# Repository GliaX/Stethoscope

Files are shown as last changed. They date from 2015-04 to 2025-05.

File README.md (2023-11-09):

Stethoscope
===========

This project aims to create a research-validated stethoscope whose plans are 
available freely and openly. The goal is for the bell to cost ~USD$1-2 to produce, 
and the rest of the stethoscope to cost approximately the same. You can see the peer-reviewed publication relating to this stethoscope's validation here:

http://journals.plos.org/plosone/article?id=10.1371/journal.pone.0193087

Currently, the stethoscope resulting from this project functions as well as the 
market gold standard, the Littmann Cardiology III.

Bill of Materials
=================

**Printed parts:**
* 1 stethoscope head (head.stl)
* 2 ear tubes (eartube.stl)
* 1 Y-piece (y_piece.stl)
* 1 Spring (spring.stl)
* 1 Ring (ring.stl)

**Other hardware:**
Some vendors are suggested.
* 40cm - 50cm Silicone 13mm (preferred) or 12mm OD, 8mm ID, 50 durometer
  * [8MM I.D X 13MM O.D NGP60 Clear Translucent Silicone Hose Pipe Tubing](https://www.advancedfluidsolutions.co.uk/8mm-id-x-13mm-od-clear-transulcent-silicone-hose-pipe-tubing-2482-p.asp) (USD$7.34/meter)

* 20cm Silicone 8mm (preferred) or 6mm OD, 4mm ID (cut into 10cm pieces), 60 durometer
  * [4mm ID x 8mm OD](https://www.advancedfluidsolutions.co.uk/4mm-id-x-8mm-od-clear-transulcent-silicone-hose-pipe-tubing-2454-p.asp)

* Diaphragm: 40mm diameter cut from a report cover with approx 0.35mm plastic sheet
  * [In Business Report Covers](https://www.amazon.com/dp/B0CJCBC86X?_encoding=UTF8&psc=1&ref_=cm_sw_r_ud_dp_CY0Q8HRSQEBTA39H9VF2)(USD$8.99)
  * You can cut the diaphragm by hand or with a stamp like [this one](https://www.amazon.ca/Karujimu-ki-jumbo-craft-circle-CN45004/dp/B001CBY41W)

* Earbuds / Eartips: Any large-sized standard earbuds will do.
  * [Silicone Earbuds 7 Pairs - Large size](https://www.amazon.ca/gp/product/B006VELFJY)
 
**Optional hardware**:
* Metal spring for holding ear tubes together

Print Instructions
==================
**INFILL MUST BE 100%** **INFILL MUST BE 100%** **INFILL MUST BE 100%** **INFILL MUST BE 100%**

* Use PETG or ABS
* Layer height: 0.2mm
* Use PrusaSlicer 2.0 or above to import 3MF file
* Modify filament and printer settings as needed.
* **DO NOT MODIFY PRINT SETTINGS**
* Export and print

Troubleshooting
===============

* If the spring and eartubes do not fit well, go ahead and scale the spring as needed
* If the head and ring do not fit well, use caution as you may be modifying the acoustics. You can scale the head a little.

Notes
=====

* We do not use PLA due to deformation in heat and poor plastic quality in the spring causing early failure. PLA may be used, but the lifetime of the stethoscope will decrease significantly.

* We do not use brims, but you may print the eartubes and Y-pieces with a brim of 2mm to ensure that none of the parts lift off.

**INFILL MUST BE 100%** **INFILL MUST BE 100%** **INFILL MUST BE 100%.** Otherwise, the stethoscope will not produce a correct sound.

Assembly Instructions
=====================

See [this instructional video](https://www.youtube.com/watch?v=u-KNTc0POLA) for assembly instructions.

* Attach the diaphragm (40mm) to the stethoscope head.
* Attach the stethoscope head to the silicone tube.
* Attach the silicone tube to the Y-Piece.
* Attach spring to ear tubes.
* Attach the Y-piece to the ear tubes.
* Attach the ear tubes to the eartips / earbuds.
* Test the stethoscope as per the validation instructions.

Printing the inserts
====================
The inserts are included in the `manual` directory. Using 8.5 x 11 (Legal) paper,
they can be printed at 8.25" page width with 95% scale for the top print and 
90% scale for the bottom print using GIMP.

The top insert is cut at 14.5cm and again at 1cm creating two labels of 13.5cm height.
These inserts are printed on adhesive material.

The bottom insert is cut at a width of 20cm with a height cuts at 25cm, 15cm, 
13.5cm and 3.5cm creating 10cm x 20cm inserts.

Changing and creating SCAD files
================================

[CrystalSCAD](https://github.com/Joaz/CrystalScad) and [OpenSCAD](http://www.openscad.org/) 
were used to create all STL files. To recreate the stethoscope head, simply do:

``` shell
gem install crystalscad
ruby source_files/stethoscope_head/stethoscope_head.rb
```

The SCAD files output from CrystalSCAD are found in `source_files/stethoscope_head/output` and are named as follows:
* PrintableStethoscopeHead1Assembly_output.scad - The head

Mass Manufacturing
==================
We generally print 4 stethoscopes per plate to ensure that each stethoscope is created out of the same material.

Our serial numbering system consists of two parts. The last number part is the total number of unique stethoscopes created since day 1. All numbers before that dash are spool identifiers involved in that stethoscope. For example:

001-010 would be the tenth stethoscope made with the first spool in our inventory. If the first spool makes a total of 15 stethoscopes, then the first stethoscope of the second spool would be 002-016. If the twentieth stethoscope uses plastic from spool 002 and spool 003, it would be 002-003-020.

Other stethoscopes
==================
Others have made 3D printed stethoscopes too. See:
* https://www.youmagine.com/designs/stethoscope-chestpiece

Licensing notes
===============
As per our understanding, hardware is not covered by copyright. However, we present
our work under the TAPR OHL license insofar as it applies.

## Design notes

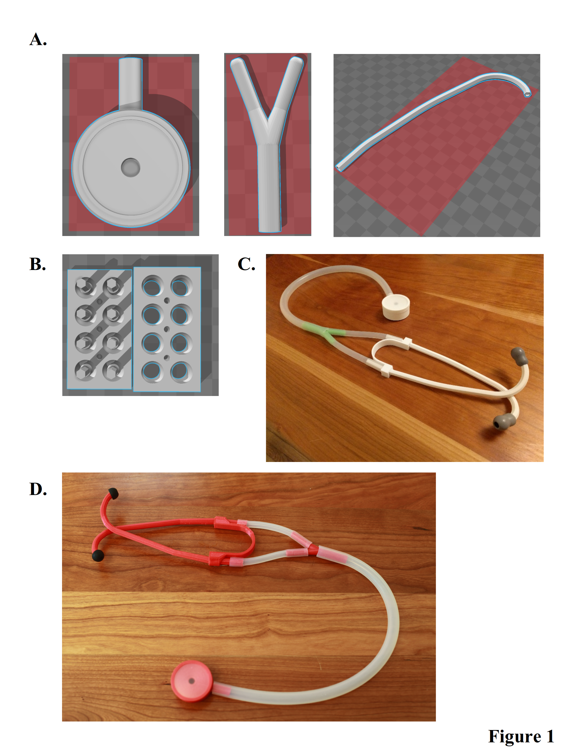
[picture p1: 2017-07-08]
Publication/Figure 1.tif

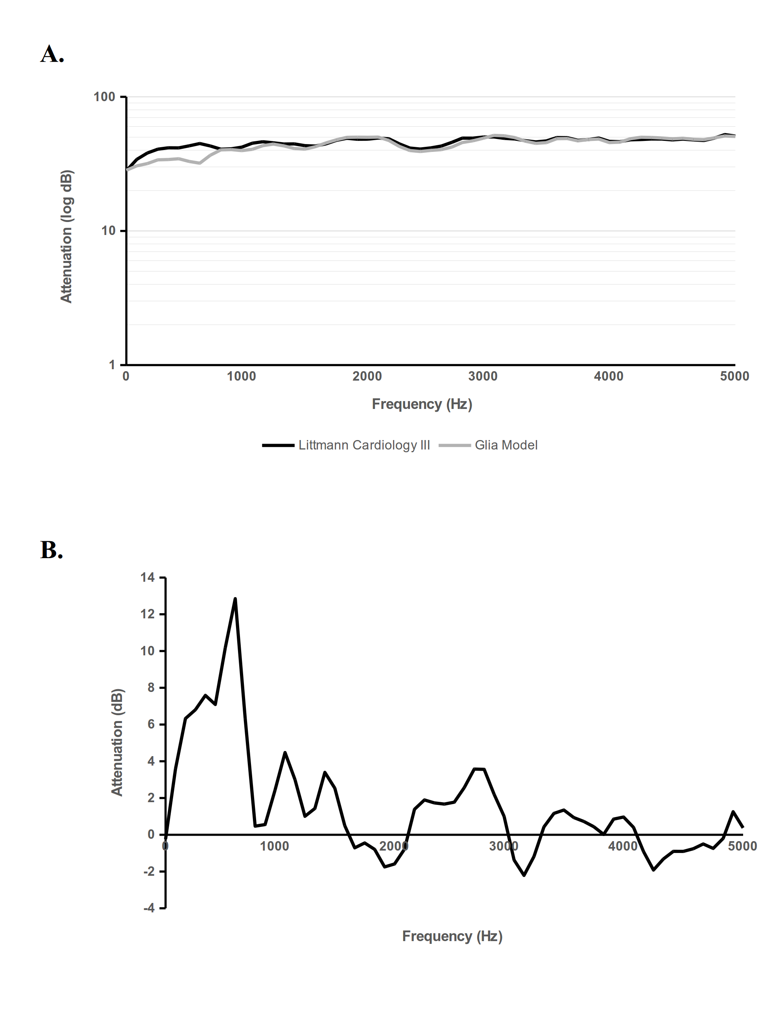
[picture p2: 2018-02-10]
publication/Fig2.tif

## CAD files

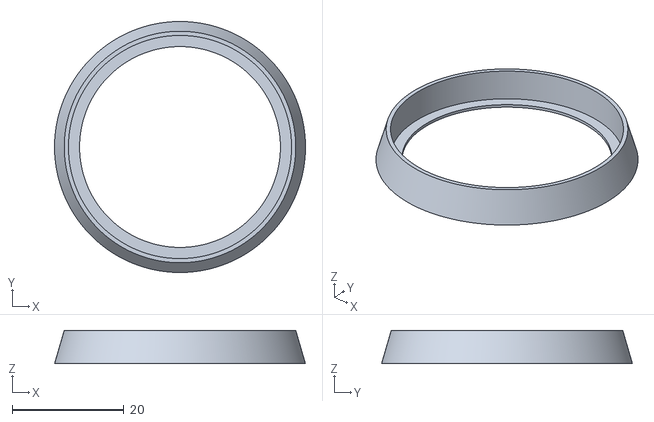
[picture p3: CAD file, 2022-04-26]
source_files/stl/ring.stl
45.0 x 45.0 x 6.00

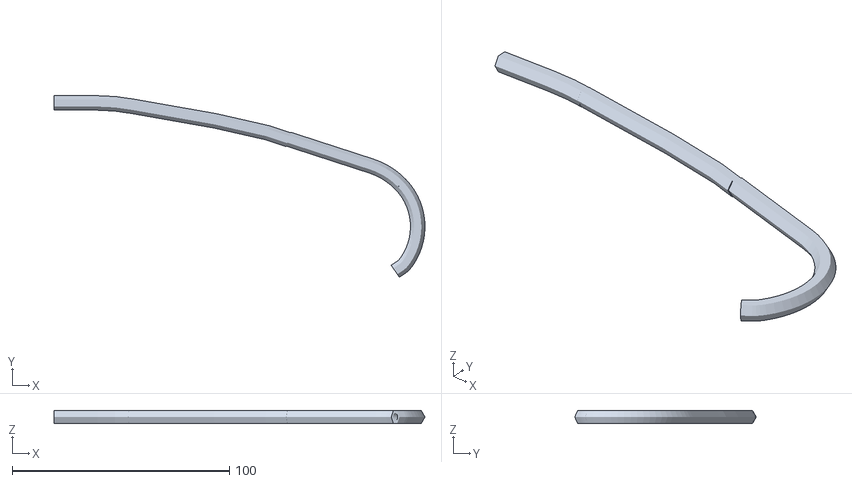
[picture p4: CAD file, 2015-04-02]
stethoscope_head/eartube.stl
170.8 x 83.6 x 5.80

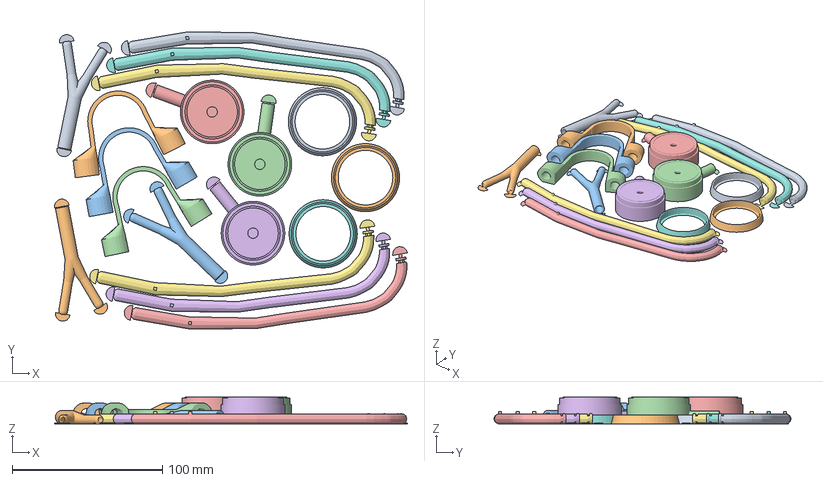
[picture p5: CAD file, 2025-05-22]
stethoscope_x3.3mf
235.1 x 198.1 x 17.9 mm
y_piece.stl
head.stl
eartube.stl x 2
Spring.stl
stetho-ring V2 FreeCad.stl

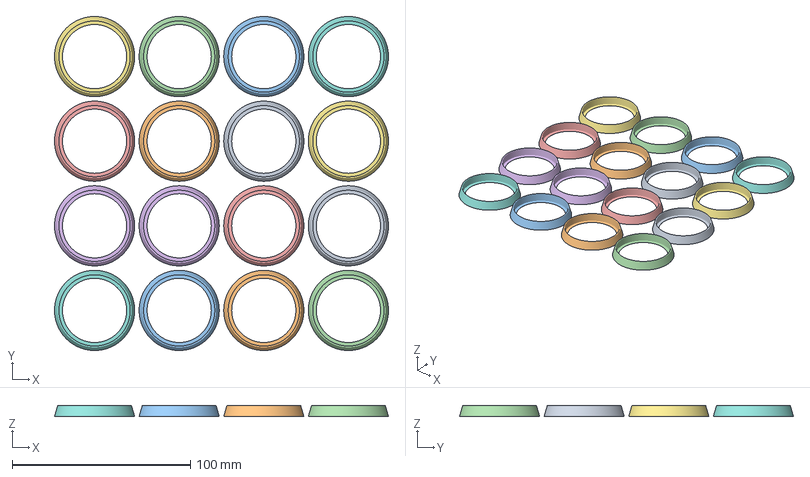
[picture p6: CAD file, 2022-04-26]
ring_x16.3mf
187.5 x 187.5 x 6.00 mm

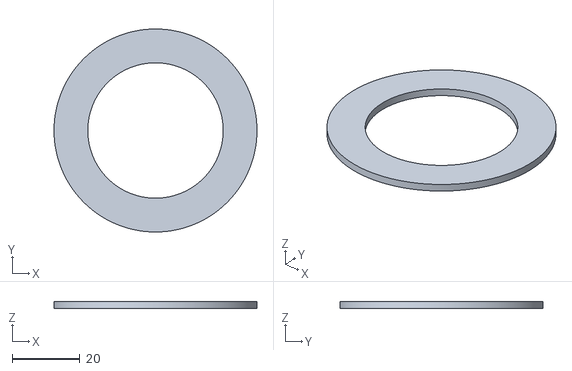
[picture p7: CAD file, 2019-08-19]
source_files/stl/Head Diaphragm Template(Cutting Guide).stl
60.0 x 60.0 x 2.00

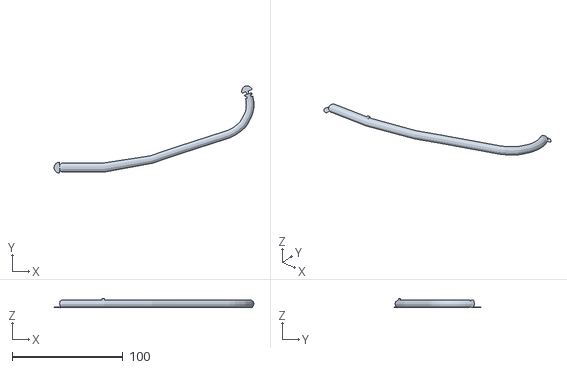
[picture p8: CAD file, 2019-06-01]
source_files/stl/eartube.stl
180.8 x 79.0 x 8.39

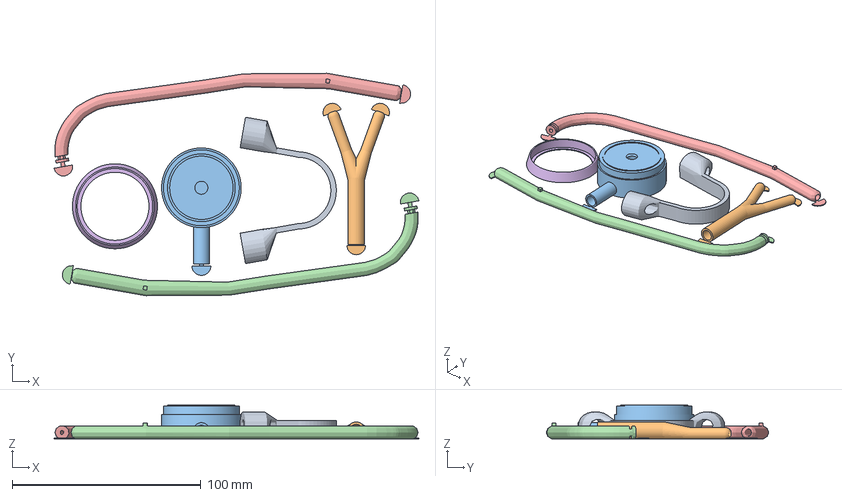
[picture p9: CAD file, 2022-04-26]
stethoscope_x1.3mf
193.3 x 117.8 x 17.9 mm
spring.stl
y_piece.stl
head.stl
eartube.stl
ring.stl

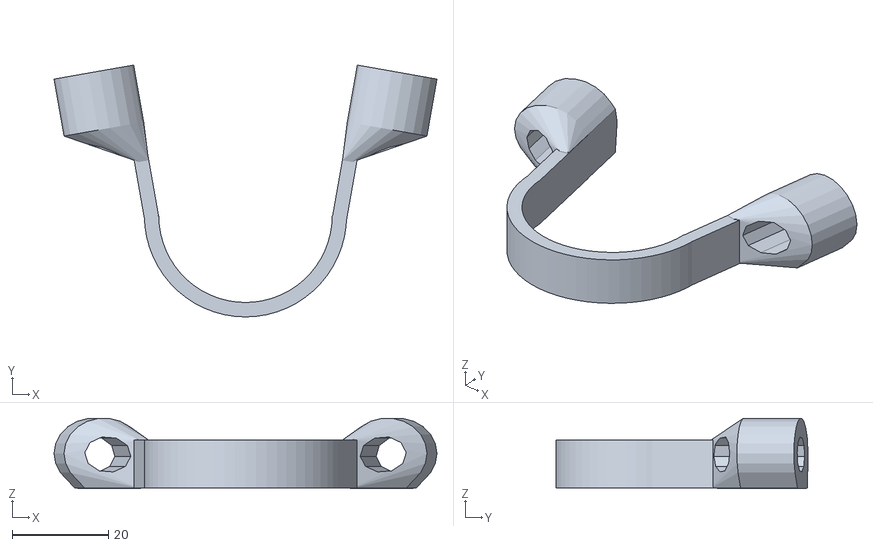
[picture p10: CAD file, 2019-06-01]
source_files/stl/spring.stl
79.5 x 52.3 x 14.6

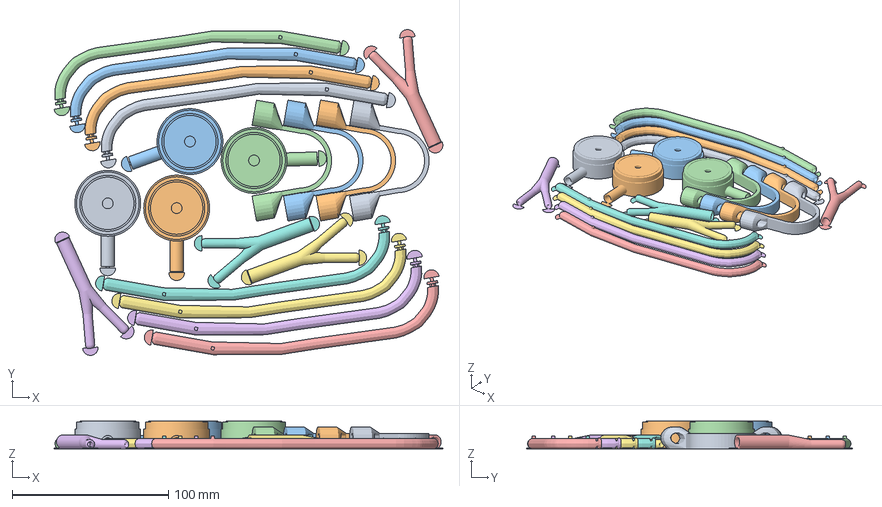
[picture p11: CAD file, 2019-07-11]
stethoscope_x4.3mf
249.1 x 208.8 x 17.9 mm
spring.stl
y_piece.stl
head.stl
eartube.stl

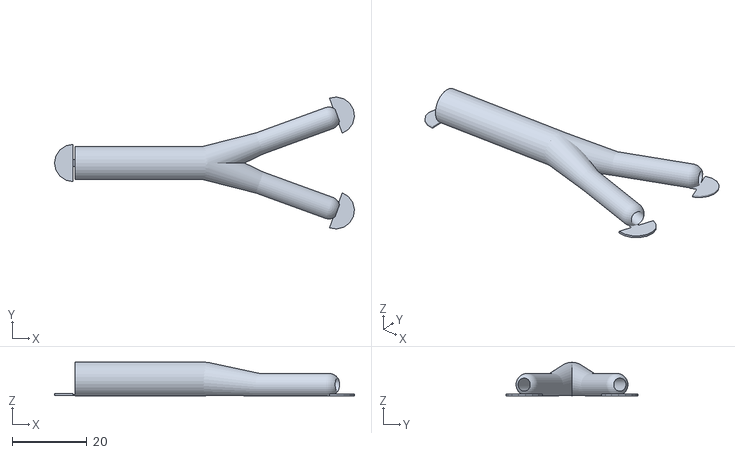
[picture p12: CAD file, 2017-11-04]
source_files/stl/y_piece.stl
80.3 x 35.3 x 9.00

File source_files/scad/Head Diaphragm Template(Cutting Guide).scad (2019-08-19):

//Head Diaphragm Template(Cutting Guide)
$outside_width = 30; //Radius of outside wall (mm)
$inside_width_wall = 20; //Inside radius of wall (mm)
$fn=360;


// Side wall

    difference() {
        cylinder(h = 2, r = $outside_width);
        cylinder(h = 2, r = $inside_width_wall);
    }

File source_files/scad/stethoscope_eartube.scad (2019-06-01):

/*
  The eartube is made of combination of spheres of 7mm diameter combined together to form its shape.
  The positioning of the spheres is taken by making array of x axis positions and array of y axis positions.
  The earbud area is different from the rest of the eartube body so it was made in different way. It is shaped and rotated to be in the right direction to snap fit standard earbuds.
  The inner hole in the eartube which should deliver the "sound" is made also from spheres but with 4mm  diameter with the same positioning of the outer shell spheres.
  The start and the end of the eartube have  mouse ears to prevent the eartube from warping during the printing process which can be removed easily by a sharp blade.
*/

/////////////////////////////////////////////////////////////
// Arrays for the X and Y positions of the spheres that make up the eartube

xarray=[-6,0,36.5,42.19,79.92,99.81,148.63,150,153.73,154.75,155.89,157.91,159.74,161.04,162.34,163.4,163.94,164.37,165.09,165.65,166.29,167.14,167.73,168.32,168.81,169.17,169.35,169.3,168.9,168.47,167.83,167.32];

yarray=[0,0,0,0.85,7.29,14.11,29.85,30.29,32.11,32.6,33.41,34.83,36.42,37.46,38.68,40.03,41.05,41.71,43.01,44.01,45.19,46.74,48.18,49.63,51.78,53.91,56.05,59.24,61.43,63.81,66.11,67.92];

// How much the earbud is rotated downward
earbud_rotation = -70;

// Width of piece connecting eartube to mouse ears for printing stability
mouse_ear_connector_width = 2;


//This difference function cuts inside the eartube body
difference(){
    // This union constucts the eartube body outer shell, which is made in two steps:
    //   1. Make the spheres to build most of its body; and
    //   2. The earbud tip at the end

    union(){
        // This difference function cuts the cylindrical insert of the earbud to snap in the eartube
        difference(){
            union(){
                // Build the shape of the outer shell of the ear tube up to the ear bud area
                // This uses the above array to create all segments
                for(i=[3:1:30]){
                    
                    //Combine eartube spheres to shape the body
                    hull(){
                        translate([xarray[i],yarray[i],0])sphere(3.5,$fn=10);
                        translate([xarray[i+1],yarray[i+1],0])sphere(3.5,$fn=10);
                    }
                }
                
                // Build the eartube base, which will be a stretched/elliptical cylinder to fit as a key in the ear tube spring. This will reduce the need for directional calibration in the assembly process.
                hull(){
                    //To create a taper, decrease the sphere size and reduce Z by the same amount so it remains on the plate. For example, to taper by 1mm, do:
                    // translate([xarray[1],yarray[1],-1])scale([1,1.2,1])sphere(2.5,$fn=10);
                    translate([xarray[1],yarray[1],0])scale([1,1.2,1])sphere(3.5,$fn=10);
                    translate([xarray[2],yarray[2],0])scale([1,1.2,1])sphere(3.5,$fn=10);
                }
                
                // Join the stretched cylinder to the rest of the eartube body without a noticable bump
                hull(){
                    translate([xarray[2],yarray[2],0])
                     scale([1,1.2,1]) sphere(3.5,$fn=10);
                    translate([xarray[4],yarray[4],0])
                     sphere(3.5,$fn=10);
                }
            }

        translate([xarray[30]-2,yarray[30]+6.5,0],0)
            rotate([0,90,earbud_rotation])cylinder(r=6,h=9.5);//earbud
        }
        
        // Add earbud connector piece
        // Build the earbud area
        translate([xarray[30]-0.4,yarray[30]+0.5,0])
         rotate([0,90,earbud_rotation])
         cylinder(r=1,h=1);
    
        translate([xarray[30]-0.4,yarray[30]+0.5,0])
         rotate([0,90,earbud_rotation]) rotate([0,0,18]) cylinder(r=3.5,h=1.5);
        
        // Build earbud snap fit cylinder joint
        translate([xarray[30]-0.4,yarray[30]+0.5,0])
         rotate([0,90,earbud_rotation]) cylinder(r=2,h=3.5);
    }
    
    union(){
        // Build the hole of the tube from the [0,0] until the earbud area

        // If tapered, point down the hollow part for the tapered part of the eartube like so:
        /*
        hull(){
            translate([xarray[0],yarray[0],-1])
                 sphere(2,$fn=10);
            translate([xarray[1],yarray[1],-1])
                 sphere(2,$fn=10);
            translate([xarray[2],yarray[2],0])
                 sphere(2,$fn=10);
        }
        */
        
        //If there is a taper, then start at part 2 of the array. Otherwise, start at 0

            for(i=[0:1:27]){
                hull(){
                translate([xarray[i],yarray[i],0])
                 sphere(2,$fn=10);
                translate([xarray[i+1],yarray[i+1],0])
                 sphere(2,$fn=10);
            }
        }
    
        // Build the shape of the hole of the tube at the earbud connector
        translate([xarray[30]-0.4,yarray[30]+0.5,0])
         rotate([0,90,earbud_rotation])cylinder(r=1.2,h=4.5,$fn=360);
    }
}

        //This creates the bottom mouse ear of the tube for added printing ease
        translate([-5,-mouse_ear_connector_width/2,-3.33])
        cube([10,mouse_ear_connector_width,0.2]);
        translate([-3,0,-3.33]) difference(){
            cylinder(r=5,h=.5);
            translate([0,-6,0]) cube([12,12,1]);
        }
        
        //Earbud mouse ear
        translate([xarray[30]-0.4,yarray[30]+0.5,0])
         rotate([0,0,earbud_rotation])
         translate([0,0,-3.33]) {
             translate([-2.5,0,0]) difference(){
                 cylinder(r=5,h=.5);
                 translate([0,-6,0]) cube([12,12,1]);
             }
             translate([-5,-mouse_ear_connector_width/2,0]) cube([5,mouse_ear_connector_width,.2]);
         }
         
         // Add stop so that people don't push the eartube too far
         translate([35.5,-1,3]) cube([2,2,2]);

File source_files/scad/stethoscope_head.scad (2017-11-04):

$fn=365;

// Take output for original head and put it in one module
module original_head() {
    union(){translate(v = [0, 0, 17.8])
    mirror(v = [0, 0, 1])
    difference(){union(){intersection(){translate(v = [-50.0, -50.0])
    cube(size = [100, 100, 17.8]);
    union(){cylinder(h = 1.080, r = 21.715);
    translate(v = [0, 0, 1.08])
    cylinder(h = 1.060, r = 21.000);
    translate(v = [0, 0, 2.14])
    cylinder(h = 0.800, r = 22.150);
    translate(v = [0, 0, 2.9400000000000004])
    cylinder(h = 3.260, r1 = 22.150, r2 = 10.500);
    translate(v = [0, 0, 6.2])
    cylinder(h = 1.300, r1 = 10.500, r2 = 8.475);
    translate(v = [0, 0, 7.5])
    cylinder(h = 13.500, r1 = 8.475, r2 = 13.500);
    translate(v = [0, 0, 21.0])
    cylinder(h = 4.000, r1 = 13.500, r2 = 16.375);
    translate(v = [0, 0, 25.0])
    cylinder(h = 0.800, r = 15.500);
    translate(v = [0, 0, 25.8])
    cylinder(h = 1.420, r = 17.215);
    translate(v = [0, 0, 13.5])
    rotate(a = [90, 0, 0])
    difference(){union(){cylinder(h = 20, r = 5.450);
    translate(v = [0, 0, 20])
    difference(){cylinder(h = 20.300, r = 4.250);
    translate(v = [0, 0, 13.8])
    union(){cylinder(h = 6.500, r1 = 2.500, r2 = 3.250);
    translate(v = [0, 0, 6.5])
    cylinder(h = 1, r = 3.250);
    }
    }
    }
    translate(v = [0, 0, -0.01])
    cylinder(h = 40.320, r = 2.650);
    }
    }
    }
    cylinder(h = 17.800, r = 21.000);
    }
    union(){translate(v = [0, 0, -0.01])
    difference(){cylinder(h = 0.570, r = 20.450);
    translate(v = [0, 0, -0.01])
    cylinder(h = 0.590, r = 17.850);
    }
    translate(v = [0, 0, 0.56])
    union(){translate(v = [0, 0, 2.735])
    mirror(v = [0, 0, 1])
    rotate_extrude(convexity = 10){polygon(points = [[0.0, 0], [0.25, 0], [0.5, 0], [0.75, 0], [1.0, 0], [1.25, 0.16], [1.5, 0.46], [1.75, 0.72], [2.0, 0.85], [2.25, 0.93], [2.5, 0.96], [2.75, 0.99], [3.0, 1.02], [3.25, 1.05], [3.5, 1.085], [3.75, 1.12], [4.0, 1.15], [4.25, 1.18], [4.5, 1.215], [4.75, 1.2475], [5.0, 1.278], [5.25, 1.308], [5.5, 1.34], [5.75, 1.372], [6.0, 1.401], [6.25, 1.432], [6.5, 1.465], [6.75, 1.5], [7.0, 1.529], [7.25, 1.559], [7.5, 1.5925], [7.75, 1.63], [8.0, 1.659], [8.25, 1.69], [8.5, 1.7225], [8.75, 1.76], [9.0, 1.7875], [9.25, 1.811], [9.5, 1.849], [9.75, 1.88], [10.0, 1.91], [10.25, 1.94], [10.5, 1.9725], [10.75, 2.005], [11.0, 2.035], [11.25, 2.065], [11.5, 2.1], [11.75, 2.134], [12.0, 2.1675], [12.25, 2.199], [12.5, 2.23], [12.75, 2.2625], [13.0, 2.291], [13.25, 2.32], [13.5, 2.3575], [13.75, 2.39], [14.0, 2.42], [14.25, 2.45], [14.5, 2.48], [14.75, 2.518], [15.0, 2.5475], [15.25, 2.5775], [15.5, 2.6125], [15.75, 2.6475], [16.0, 2.68], [16.25, 2.735], [16.7, 2.735], [0, 2.735]]);
    }
    translate(v = [0, 0, -2])
    cylinder(h = 2, r = 16.700);
    }
    translate(v = [0, 0, 13.5])
    rotate(a = [90, 0, 0])
    translate(v = [0, 0, -0.01])
    cylinder(h = 40.320, r = 2.650);
    translate(v = [0, 0, -0.01])
    cylinder(h = 27.240, r = 3.440);
    }
    }
    cylinder(h = 1.700, r = 5.000);
    }
}

//Create ring to subtract
module ring () {
    translate([0,0,12.8])
    difference() {
        cylinder(h = 6, r = 25);
        cylinder(h = 6, r = 20);
    }
}

// Create final model by subtracting ring from head
difference() {
    original_head();
    ring();
}



translate([-1,-40.2-2.5,.05])cube([2,5,.2]);
translate([0,-40.2-1,.05])difference(){
    cylinder(r=5,h=.5);
    translate([-6,0,0])cube([12,12,1]);
}

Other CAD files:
source_files/scad/stethoscope_metallic_spring_holder.scad
source_files/scad/stethoscope_ring.scad
source_files/scad/stethoscope_spring.scad
source_files/scad/stethoscope_y-piece.scad

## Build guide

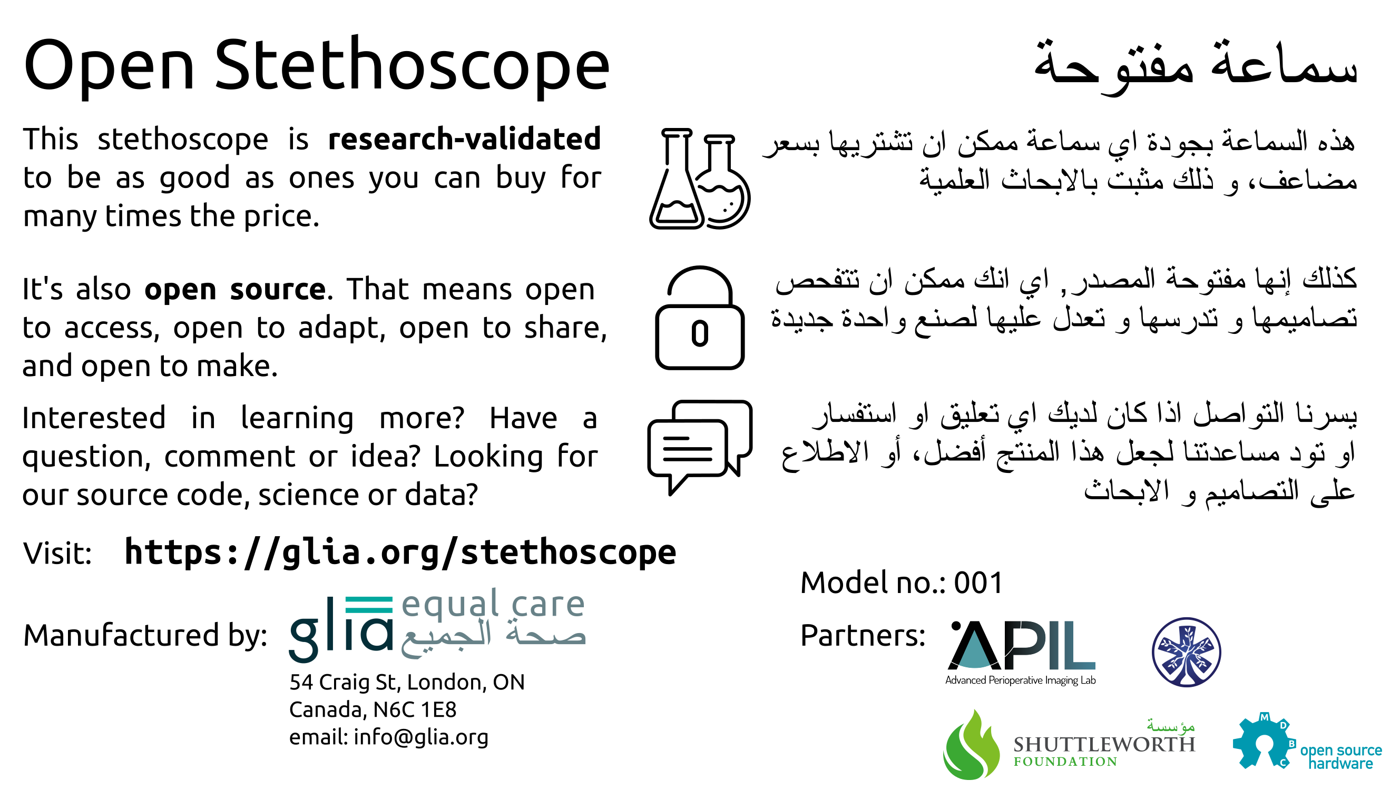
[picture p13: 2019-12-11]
manual/box-insert_top.png

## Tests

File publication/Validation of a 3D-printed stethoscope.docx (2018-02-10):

# Validation of an effective, low cost, Free/open access 3D-printed stethoscope

Alexander Pavlosky¹, Jennifer Glauche⁶, Spencer Chambers¹, Mahmoud Al-Alawi⁵, Kliment Yanev⁶, Tarek Loubani1,2,3,4,5*

¹ Faculty of Medicine, University of Western Ontario, London, Ontario, Canada.

² Division of Emergency Medicine, Department of Medicine, University of Western Ontario, London, Ontario, Canada.

³ Division of Emergency Medicine, London Health Sciences Centre, London, Ontario, Canada

⁴ Division of Emergency Medicine, Al-Shifa Hospital, Gaza City, Occupied Palestinian Territories

⁵ Glia, Inc., London, Canada

⁶ No institutional affiliation (Independent contractors), Cologne, Germany

* Corresponding author

E-mail: tarek@tarek.org

# Abstract

The modern acoustic stethoscope is a useful clinical tool used to detect subtle, pathological changes in cardiac, pulmonary and vascular sounds. Currently, brand-name stethoscopes are expensive despite limited innovations in design or fabrication in recent decades. Consequently, the high cost of high quality, brand name models serves as a barrier to clinicians practicing in various settings, especially in low- and middle-income countries. In this publication, we describe the design and validation of a low-cost open-access (Free/Libre) 3D-printed stethoscope which is comparable to the Littmann Cardiology III for use in low-access clinics.

# Introduction

Since its introduction in 1819 by René Laennec[1], the acoustic stethoscope has been an integral part of clinical medicine. Despite the lack of major structural design innovations over recent decades, modern stethoscopes can be an expensive part of the physician’s armamentarium, often costing several hundred US dollars. The high cost of modern stethoscopes remains a significant barrier to physicians and allied health professionals practicing in the developed word and in low- and middle-income countries, where few affordable high-quality options exist. Traditionally, the selection of a stethoscope often does not involve the acoustic properties of the model[2] with most users selecting an expensive brand-name stethoscope such as the Littmann Cardiology III or other premium brands. However, previous studies that compared stethoscope brands have concluded that cost does not correlate with better diaphragm sound quality at relevant frequencies, compared with lower-cost alternatives[3,4]. While other 3D printed stethoscope models that would be low-cost to produce can be found online[5–15], we are not aware of any that have been used clinically or research-validated.

Numerous groups have previously attempted to standardize methods to determine the efficacy of acoustic stethoscope models[2,16–20], but currently no accepted standardized modality exists. Consequently, the performance of any acoustic stethoscope is little more than the manufacturer’s claim or the subjective opinion of the user. Some groups have attempted to objectively compare acoustic stethoscope models and currently two competing methods of measuring frequency response exist. The first method uses air coupling to transmit frequencies[2–4,16,17] while the other uses a phantom to simulate vibrations of the chest wall[19,21,22]. These methods allow investigators to quantitatively compare the sensitivity of a stethoscope model compared with another.

In this article, we describe the construction and validation of a low cost, Free/open access 3D printed acoustic stethoscope - referred to here as the ‘Glia model’. The aim of this research is to give low budget health care systems affordable access to an effective stethoscope for a cost under $5 USD and to contribute to the body of literature by ensuring this stethoscope is rigorously tested and released as Free/open access hardware. To achieve this, we utilized 3D printing, a technology that is advancing rapidly and becoming increasingly inexpensive[23]. 3D printing technology has been used by others, especially for work on prosthetics[24–26], splints[27,28] and preoperative planning[29]. It has also been proposed as a partial solution to problems in supply chain management during disasters[30], such as by Global Humanitarian Lab[31] and Field Ready[32]. The flexibility of 3D printing technology also allows users to augment our design to fit their own needs. We also attempt to make our bills of material, construction methodology and validation methods accessible and low cost, allowing others to validate our design independently with ease.

# Methods

## Stethoscope design

Design of the Glia model 3D printed stethoscopes was done using Free/Open Source Software (FOSS) so as to keep costs low and allow others easy access to examine and modify code. CrystalSCAD (https://github.com/Joaz/CrystalScad, Germany) was used to create digital models of the stethoscope head, two ear tubes and an ear plug mold due to its ability to create complex shapes in a way that was not possible with OpenSCAD at the time. OpenSCAD (http://openscad.org, Canada) was used to create digital models of the Y-piece, stethoscope ring and spring (Fig 1A). Since its original creation as documented in this paper, the eartubes have been completely ported to OpenSCAD. The stethoscope head is presently a hybrid of CrystalSCAD and OpenSCAD. As the ear plug mold is no longer used in our current production process, its archived version also remains in CrystalSCAD.

Other accessory hardware is required, such as the plastic diaphragm, tubing and ear buds. These are listed in Table 1.

Fig 1. Computer aided design and assembly of the 3D printed stethoscope. Digital models of the 3D printed stethoscope parts are shown in Fig 1A. From left to right: the head, Y piece and ear tube are shown. An earplug mold design is also shown in Fig 1B. Each part was 3D printed in ABS, with the assembled stethoscope is shown in Fig 1C using the bill of materials listed in Table 1.

All print designs can be downloaded for free at https://github.com/GliaX

## Stethoscope printing and assembly

Each part was printed on a commodity 3D printer (Prusa Mk II, 1.75 mm filament diameter, 0.4 mm nozzle diameter, no scaffolding or support) using acrylonitrile butadiene styrene (ABS) with 100% infill as indicated and 0.2 mm layer height. A 40 cm silicone 12 mm outer diameter (OD), 8 mm inner diameter (ID) tube was attached between the stethoscope head and the larger bore of the Y piece. Two 9 cm silicone 6 mm OD, 4 mm ID tubes were attached between the smaller bore of the Y piece and the ear tubes. A diaphragm was cut from a Staples brand PVC report cover (Swing-lock report cover, clear with black spine; UPC 718103160223) by turning a sharp caliper and creating a circular diaphragm with a 40 mm diameter. This diaphragm was attached to the stethoscope head with a printed ABS ring. A printed ABS truss that has some spring properties by design is used as a spring for the ear tubes.

The earbuds are generic earbuds from commodity earbud-style headphones that are widely available and of negligible cost. The final construction of the current model can be seen in Fig 1C.

Costs in Table 1 were calculated using the density of PA757 ABS (1.05 g/cm³)[33] and the part weight, which is calculated using version 1.3.0-dev of the Slic3r software (https://slic3r.org, Italy). We assumed the price of 12 lbs (5.4545 kg) of virgin PA757 ABS pellets to be $38.99 USD[34]. Commercial ABS filament was assumed to cost $23.96 USD/kg[35]. Electricity costs were estimated using the Ontario Energy Board's current mid-peak rates[36,37] multiplied by the printer's expected electricity use based on measurements of a similar printer with similar temperatures[38] printing for four hours then multiplied by 0.8 for an approximate conversion to US currency. This number was rounded up to the nearest cent. The energy costs of filament extrusion are negligible when estimated based on previous reporting[39] and were thus not included.

## Acoustic transfer

The frequency response of Glia model stethoscopes, compared with the Littmann Cardiology III, was determined using an experimental setup modeled from a phantom-based frequency response setup previously described[19]. A latex balloon filled with 2 L (2000 g) of water was used as a phantom and each stethoscope was applied to the surface by hand. Phantom excitations were supplied by an external vibrating speaker which was placed in contact with the balloon and sound was played at 86 Hz intervals between 0 and 5000 Hz (white noise) for 15 seconds. The output of each stethoscope was recorded by a microphone which was placed in a silicon tube attached to the stethoscope head for spectral analysis. Spectral analyses such as these have been used successfully in the past to analyze breath sounds recorded from individuals with lung pathology[40]. The simplicity of this design was intended to allow other users to validate our design independently.

# Results

After many iterations, we successfully designed a working stethoscope, known as the Glia model (Fig 1), at a total cost of $2.83 USD using recycled ABS pellets. A bill of materials and cost breakdown can be found in Table 1.

Item | Dimensions (mm) | Weight (g) | Cost using ABS pellets (USD) | Cost using ABS filament (USD)
Stethoscope head | 44.30 x 62.45 x 17.80 | 23.82 | $0.17 | $0.57
Stethoscope Y piece | 70.89 x 29.94 x 9.00 | 2.84 | $0.02 | $0.07
Stethoscope ear tubes | 170.79 x 83.62 x 5.80 | 12.52 | $0.09 | $0.30
Stethoscope ring | r = 21, h = 7 | 0.81 | $0.01 | $0.02
Stethoscope spring | 91.25 x 111.62 x 15.05 | 8.05 | $0.06 | $0.19
Silicone tubing | L = 400 – 12 OD, 8 ID 2 x L = 90 – 6 OD, 4 ID | | $1.93 | $1.93
Diaphragm | r = 20 | | $0.06 | $0.06
Silicone earbuds | n/a | | $0.02 | $0.02
Electricity usage | 0.5 KWh at mid-peak rates | | $0.04 | $0.04
Total | | | $2.40 | $3.20

Table 1. Bill of materials for the Glia model stethoscope (100% infill)

We compared the Glia stethoscope to the Littmann Cardiology III using a phantom, as described in the methods. At all frequencies tested, the Glia model performed similarly to the Cardiology III (Fig 2A). The difference in attenuation (dB) of the Glia model to the Littmann Cardiology III is shown in Fig 2B with values greater than 0 dB indicating that the Glia attenuated less sound.

Fig 2. Calibration and comparison of 3D printed Glia model stethoscopes to the Littmann Cardiology III. Stethoscope output responses were measured using the equipment setup described in the methods. Each stethoscope model recorded input sound at multiple frequencies and the change in amplitude between input and recorded sound was documented (lower log attenuation is better) for each stethoscope (Fig 2A). The decibel difference in attenuation (Glia minus Littmann) is shown across all frequencies tested where values above 0 dB indicate the Glia model attenuated less sound (Fig 2B).

# Discussion

Using a phantom-based method, we show here that the Glia model stethoscope, at a cost of $2.40 USD, is comparable to the Littmann Cardiology III across a range of spectral frequencies from 86 Hz to 5000 Hz, making it a low-cost, suitable alternative to those who cannot access or afford a high-cost model.

The stethoscope is one of the most widely used instruments in modern medicine, allowing clinicians to detect subtle changes in heart, lung and vascular sounds. Despite a lack of major innovation in design or fabrication since Dr. Littmann patented his stethoscope in 1963, the acoustic stethoscope remains an expensive piece of equipment that creates a cost barrier for physicians practicing in low- and middle-income countires. This study aims to create a validated high quality acoustic stethoscope at a cost under $5 USD.

The quality and intensity of the sound reaching the earpiece from the diaphragm is dependent on nearly every piece of the stethoscope as well as the physiology of the user. These variables have been previously summarized[3] and include the size and volume of the bell[18,41]; hardness of the inner cavity of the bell[42]; improperly fitted components allowing air leaks and loss of sound[41]; the thickness, size and tautness of the diaphragm and the interior smoothness, rigidity, length and diameter of the tubing[43,44]. Additional user related factors include improperly fitted ear pieces that allow air exchange[4,41,44,45]; anatomical variations of the auditory canal of the user[45]; background noise[46] and training[47]. Many of these variables needed to be considered when designing the Glia model stethoscope, particularly physical properties such as channel diameter through the 3D printed parts and infill percentage, which ultimately determines the density and hardness of the parts. We also tried several printing materials including poly-lactic acid (PLA) and ABS. Of particular challenge was creating the interface between the ear tube and the spring to prevent rotation when the ear tubes were pulled apart.

As previously mentioned, no standard method of determining the acoustic response of stethoscope models currently exists. Previous studies have attempted to objectively quantify stethoscope efficacy[19,21,22,41] and previous comparisons between brands indicate that no significant correlation between cost and quality exists[3,4]. However, there may be some subjective decrease in efficacy when using low-quality disposable stethoscopes[47].

The Littmann Cardiology III has recently become unavailable. Its replacement, the Littmann Cardiology IV costs $190 USD[48], which is comparable to other brand name stethoscopes such as the Welch Allyn Harvey Elite ($150 USD[49]). Ultimately, however, the usefulness of any stethoscope is dependent on user preference and so we encourage those with access to a 3D printer to build and test our model independently. The protocol listed in the methods has been purposely designed to be replicable using commonly available materials. Any printer capable of printing in ABS should be able to create our device, including RepRap printer designs used by our group[50]. Printers of sufficient quality and reliability can be easily obtained or built internationally for less than $1,000 USD[51].

The Glia model stethoscope is a class I medical device according to Health Canada and the FDA. In Canada, a non-profit company was incorporated to manufacture stethoscopes and has received a Medical Device Establishment Licence from Health Canada. The stethoscope is in clinical use in London, Canada at the London Health Sciences Centre. It has also been trialed and was gradually introduced in the Gaza strip, an area with extremely limited access to medical devices. Hospitals in Gaza are self-sufficient producers of these stethoscopes.

## Low cost does not mean low quality

This work aimed to produce a stethoscope of comparable quality to those premium-brand devices unobtainable due to economic, political or military factors. We believe this aim was achieved as shown in the results above. This work is significant in both developed and low- and middle-income countries (LMICs) as it introduces two cost-saving innovations: the use of plastic and 3D printing to create a product equal to metal alternatives and the dissemination of plans and bills of material through a Free and open source license.

Our results suggest that the use of inexpensive techniques to produce medical devices does not necessitate the lowering of quality standards. This presents a challenge to an implicit assumption found in some literature and organizations that lower standards may be necessary for the developing world[52,53]. An example pertinent to 3D printing is the use of 3D printed upper limb prosthetics based on the e-Nable project[26] in LMICs. These prosthetics have been found to be inadequate in many important activities as per a standardized assessment[54]. Despite this, the implicit argument is that poor quality devices are acceptable because of the present lack of access to devices[53].

## Future research

This project was the first of several planned open access medical device projects. Future plans include expanding access by providing validated models of other pieces of medical equipment, including pulse oximeters, tourniquets, otoscopes and ECG machines, allowing health institutions to sustainably produce affordable, high quality equipment for many clinicians.

# Acknowledgments

We would like to thank Carrie Wakem, Kristine Van Aarsen, Dr. Melanie Columbus, Dr. Jon Dreyer and the emergency departments of Al-Shifa Hospital and London Health Sciences Centre for their support of this project and its authors.

# Citations

1. Laennec RTH. De l’auscultation médiate ou traité du diagnos-tic de maladies des poumons et du coeur, fondé principalement surce nouveau moyen d’exploration. Bross Chaude Paris. 1819;

2. Johnston FD, Kline EM. An acoustical study of the stethoscope. Arch Intern Med. 1940; 328–339.

3. Abella M, Formolo J, Penney D. Comparison of the acoustic properties of six popular stethoscopes. J Acoust Soc AM. 1992; 2224–2228.

4. Kindig J, Beeson T, Campbell R, Andries F, Tavel M. Acoustical performance of the stethoscope: a comparative analysis. Am Heart J. 1982;104: 269–275.

5. Aguilera-Astudillo C, Chavez-Campos M, Gonzalez-Suarez A, Garcia-Cordero JL. A low-cost 3-D printed stethoscope connected to a smartphone. Conf Proc Annu Int Conf IEEE Eng Med Biol Soc IEEE Eng Med Biol Soc Annu Conf. 2016;2016: 4365–4368. doi:10.1109/EMBC.2016.7591694

6. Thingiverse.com. Stethoscope (with diaphram) by TheLOLNinja [Internet]. [cited 29 Jan 2018]. Available: https://www.thingiverse.com/thing:1182797

7. Thingiverse.com. Stethoscope by BWBarker [Internet]. [cited 29 Jan 2018]. Available: https://www.thingiverse.com/thing:577507

8. Thingiverse.com. Pinard Horn (Foetoscope) by fil [Internet]. [cited 29 Jan 2018]. Available: https://www.thingiverse.com/thing:15571

9. Thingiverse.com. Digital Stethoscope by riki74 [Internet]. [cited 29 Jan 2018]. Available: https://www.thingiverse.com/thing:266767

10. Thingiverse.com. Pinard Horn by DrewTM [Internet]. [cited 29 Jan 2018]. Available: https://www.thingiverse.com/thing:1014544

11. Thingiverse.com. Pinard stethoscope/horn by Imprenta3D [Internet]. [cited 29 Jan 2018]. Available: https://www.thingiverse.com/thing:1609959

12. Thingiverse.com. Stethoscope by death_metal [Internet]. [cited 29 Jan 2018]. Available: https://www.thingiverse.com/thing:233936

13. Thingiverse.com. Stethoscope by riki74 [Internet]. [cited 29 Jan 2018]. Available: https://www.thingiverse.com/thing:266747

14. Thingiverse.com. Stethoscope directional cone for engine noise finding by Sneezy3D [Internet]. [cited 29 Jan 2018]. Available: https://www.thingiverse.com/thing:1213095

15. Thingiverse.com. Toy Stethoscope by heixingxing [Internet]. [cited 29 Jan 2018]. Available: https://www.thingiverse.com/thing:2670812

16. Ertel P, Lawrence M, Brown R, Stern AM. Stethoscope acoustics. I. The doctor and his stethoscope. Circulation. 1966;34: 889–898.

17. Ertel P, Lawrence M, Brown R, Stern AM. Stethoscope acoustics. II. Transmission and filtration patterns. Circulation. 1966;34: 899–909.

18. Ertel P, Lawrence M, Song W. How to test stethoscopes. Med Res Eng. 1969;8: 7–17.

19. Watrous R, Grove D, Bowen D. Methods and results in characterizing electronic stethoscopes. Comput Cardiol. 2002; 653–656.

20. Gavish B, Heller O. A practical method for evaluating stethoscopes. Biomed Instrum Technol. 1992;26: 97–102.

21. Royston T, Zhang X, Mansy H, Sandler R. Modeling sound transmission through the pulmonary system and chest with application to diagnosis of a collapsed lung. J Acoust Soc Am. 111: 1931–1946.

22. Padmanabhan V, Semmlow J, Welkowitz W. Accelerometer type cardiac transducer for detection of low-level heart sounds. IEEE Trans Biomed Eng. 1993;40: 21–28.

23. Ventola CL. Medical Applications for 3D Printing: Current and Projected Uses. Pharm Ther. 2014;39: 704–711.

24. 3D-Printed Prosthetics for the Developing World | Autodesk Research [Internet]. [cited 30 Jan 2018]. Available: https://www.autodeskresearch.com/printedprosthetics

25. Jones GK, Rosendo A, Stopforth R. Prosthetic design directives: Low-cost hands within reach. IEEE; 2017. pp. 1524–1530. doi:10.1109/ICORR.2017.8009464

26. Enabling The Future. In: Enabling The Future [Internet]. [cited 30 Jan 2018]. Available: http://enablingthefuture.org/

27. Hoang D, Perrault D, Stevanovic M, Ghiassi A. Surgical applications of three-dimensional printing: a review of the current literature & how to get started. Ann Transl Med. 2016;4. doi:10.21037/atm.2016.12.18

28. Wong JY. On-Site 3D Printing of Functional Custom Mallet Splints for Mars Analogue Crewmembers. Aerosp Med Hum Perform. 2015;86: 911–914. doi:10.3357/AMHP.4259.2015

29. Farooqi KM, Mahmood F. Innovations in Preoperative Planning: Insights into Another Dimension Using 3D Printing for Cardiac Disease. J Cardiothorac Vasc Anesth. 2017; doi:10.1053/j.jvca.2017.11.037

30. Ibrahim AMS, Jose RR, Rabie AN, Gerstle TL, Lee BT, Lin SJ. Three-dimensional Printing in Developing Countries. Plast Reconstr Surg Glob Open. 2015;3: e443. doi:10.1097/GOX.0000000000000298

31. Global Humanitarian Lab. In: Global Humanitarian Lab [Internet]. [cited 30 Jan 2018]. Available: https://globalhumanitarianlab.org/

32. Field Ready - Humanitarian Supplies Made-in-the-Field. In: Field Ready - Humanitarian Supplies Made-in-the-Field [Internet]. [cited 30 Jan 2018]. Available: https://www.fieldready.org

33. Chi Mei Corporation. ABS PA757 Datasheet [Internet]. [cited 30 Jan 2018]. Available: http://www.chimeicorp.com/upload/att/2013-05/201305161402533576591.pdf

34. Filastruder. PA757 ABS Natural Pellets. In: Filastruder [Internet]. [cited 30 Jan 2018]. Available: https://www.filastruder.com/products/pa757-abs-pellets

35. ABS Filament - BLACK - 1.75mm. In: Filaments.ca [Internet]. [cited 30 Jan 2018]. Available: https://filaments.ca/products/abs-filament-black-1-75-mm

36. Ontario Energy Board. Electricity rates [Internet]. [cited 30 Jan 2018]. Available: https://www.oeb.ca/rates-and-your-bill/electricity-rates

37. Ontario Energy Board. Historical electricity rates [Internet]. [cited 30 Jan 2018]. Available: https://www.oeb.ca/rates-and-your-bill/electricity-rates/historical-electricity-rates

38. Walls S, Corney J, Annamalai Vasantha G. RELATIVE ENERGY CONSUMPTION OF LOW-COST 3D PRINTERS. 2014.

39. Zhong S, Pearce JM. Tightening the loop on the circular economy: Coupled distributed recycling and manufacturing with recyclebot and RepRap 3-D printing. Resour Conserv Recycl. 2018;128: 48–58. doi:10.1016/j.resconrec.2017.09.023

40. Pasterkamp H, Kraman SS, Wodicka GR. Respiratory sounds. Advances beyond the stethoscope. Am J Respir Crit Care Med. 1997;156: 974–987. doi:10.1164/ajrccm.156.3.9701115

41. Ertel P, Lawrence M, Song W. Stethoscope acoustics and the engineer: Concepts and problems. J Audio Eng Soc. 1971;19: 182–186.

42. Rappaport MB, Sprague HB. Physiologic and physical laws that govern ausculation, and their clinical application: The acoustic stethoscope and the electrical amplifying stethoscope and stethograph. Am Heart J. 1941;21: 257–318.

43. Rappaport MB, Sprague HB. The effects of tubing bore on stethoscope efficiency. Am Heart J. 1951; 605–609.

44. Rappaport MB, Sprague HB. The effects of improper fitting of stethoscope to ears on auscultatory efficiency. Am Heart J. 1952;43: 713–715.

45. Groom D. The effect of background noise on cardiac auscultation. Am Heart J. 1956;52: 781–790.

46. Groom D, Chapman W. Anatomic variations of the auditory canal pertaining to the fit of stethoscope earpieces. Circulation. 1959;19: 606–608.

47. Mehmood M, Abu Grara HL, Stewart JS, Khasawneh FA. Comparing the auscultatory accuracy of health care professionals using three different brands of stethoscopes on a simulator. Med Devices Evid Res. 2014;7: 273–281.
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

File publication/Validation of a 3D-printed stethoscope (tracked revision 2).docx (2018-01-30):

# Validation of an effective, low cost, Free/open access 3D-printed stethoscope

Alexander Pavlosky¹, Jennifer Glauche⁶, Spencer Chambers¹, Mahmoud Al-Alawi⁵, Kliment Yanev⁶, Tarek Loubani1,2,3,4,5*

¹ Faculty of Medicine, University of Western Ontario, London, Ontario, Canada.

² Division of Emergency Medicine, Department of Medicine, University of Western Ontario, London, Ontario, Canada.

³ Division of Emergency Medicine, London Health Sciences Centre, London, Ontario, Canada

⁴ Division of Emergency Medicine, Al-Shifa Hospital, Gaza

⁵ Glia, Inc., London, Canada

⁶ No institutional affiliation

* Corresponding author

E-mail: tarek@tarek.org

# Abstract

The modern acoustic stethoscope is a useful clinical tool used to detect subtle, pathological changes in cardiac, pulmonary and vascular sounds. Currently, brand-name stethoscopes are expensive despite limited innovations in design or fabrication in recent decades. Consequently, the high cost of high quality, brand name models serves as a barrier to clinicians practicing in various settings, especially in low- and middle-income countries. In this publication, we describe the design and validation of a low-cost open-access (Free/Libre) 3D-printed stethoscope which is comparable to the Littmann Cardiology III for use in low-access clinics.

# Introduction

Since its introduction in 1819 by René Laennec¹, the acoustic stethoscope has been an integral part of clinical medicine. Despite the lack of major structural design innovations over recent decades, modern stethoscopes can be an expensive part of the physician’s armamentarium, often costing several hundred US dollars. The high cost of modern stethoscopes remains a significant barrier to physicians and allied health professionals practicing in the developed word and in low- and middle-income countries, where few affordable high-quality options exist. Traditionally, the selection of a stethoscope often does not involve the acoustic properties of the model² with most users selecting an expensive brand-name stethoscope such as the Littmann Cardiology III or other premium brands. However, previous studies that compared stethoscope brands have concluded that cost does not correlate with better diaphragm sound quality at relevant frequencies, compared with lower-cost alternatives³,⁴. While other 3D printed stethoscope models that would be low-cost to produce can be found online⁵⁻¹⁵, we are not aware of any that have been used clinically or research-validated.

Numerous groups have previously attempted to standardize methods to determine the efficacy of acoustic stethoscope models²,¹⁶⁻²⁰, but currently no accepted standardized modality exists. Consequently, the performance of any acoustic stethoscope is little more than the manufacturer’s claim or the subjective opinion of the user. Some groups have attempted to objectively compare acoustic stethoscope models and currently two competing methods of measuring frequency response exist. The first method uses air coupling to transmit frequencies²⁻⁴,¹⁶,¹⁷ while the other uses a phantom to simulate vibrations of the chest wall¹⁹,²¹,²². These methods allow investigators to quantitatively compare the sensitivity of a stethoscope model compared with another.

In this article, we describe the construction and validation of a low cost, Free/open access 3D printed acoustic stethoscope - referred to here as the ‘Glia model’. The aim of this research is to give low budget health care systems affordable access to an effective stethoscope for a cost under $5 USD and to contribute to the body of literature by ensuring this stethoscope is rigorously tested and released as Free/open access hardware. To achieve this, we utilized 3D printing, a technology that is advancing rapidly and becoming increasingly inexpensive²³. 3D printing technology has been used by others, especially for work on prosthetics²⁴⁻²⁶, splints²⁷,²⁸ and preoperative planning²⁹. It has also been proposed as a partial solution to problems in supply chain management during disasters³⁰, such as by Global Humanitarian Lab³¹ and Field Ready³². The flexibility of 3D printing technology also allows users to augment our design to fit their own needs. We also attempt to make our bills of material, construction methodology and validation methods accessible and low cost, allowing others to validate our design independently with ease.

# Methods

## Stethoscope design

Design of the Glia model 3D printed stethoscopes was done using Free/Open Source Software (FOSS) so as to keep costs low and allow others easy access to examine and modify code. CrystalSCAD (https://github.com/Joaz/CrystalScad, Germany) was used to create digital models of the stethoscope head, two ear tubes and an ear plug mold due to its ability to create complex shapes in a way that was not possible with OpenSCAD at the time. OpenSCAD (http://openscad.org, Canada) was used to create digital models of the Y-piece, stethoscope ring and spring (Fig 1A). Since its original creation as documented in this paper, the eartubes have been completely ported to OpenSCAD. The stethoscope head is presently a hybrid of CrystalSCAD and OpenSCAD. As the ear plug mold is no longer used in our current production process, its archived version also remains in CrystalSCAD.

Other accessory hardware is required, such as the plastic diaphragm, tubing and ear buds. These are listed in Table 1.

Figure 1. Computer aided design and assembly of the 3D printed stethoscope. Digital models of the 3D printed stethoscope parts are shown in Figure 1A. From left to right: the head, Y piece and ear tube are shown. An earplug mold design is also shown in Figure 1B. Each part was 3D printed in ABS, with the assembled stethoscope is shown in Figure 1C using the bill of materials listed in Table 1.

All print designs can be downloaded for free at https://github.com/GliaX

## Stethoscope printing and assembly

Each part was printed on a commodity 3D printer (Prusa Mk II, 1.75 mm filament diameter, 0.4 mm nozzle diameter, no scaffolding or support) using acrylonitrile butadiene styrene (ABS) with 100% infill as indicated and 0.2 mm layer height. A 40 cm silicone 12 mm outer diameter (OD), 8 mm inner diameter (ID) tube was attached between the stethoscope head and the larger bore of the Y piece. Two 9 cm silicone 6 mm OD, 4 mm ID tubes were attached between the smaller bore of the Y piece and the ear tubes. A diaphragm was cut from a Staples brand PVC report cover (Swing-lock report cover, clear with black spine; UPC 718103160223) by turning a sharp caliper and creating a circular diaphragm with a 40 mm diameter. This diaphragm was attached to the stethoscope head with a printed ABS ring. A printed ABS truss that has some spring properties by design is used as a spring for the ear tubes.

The earbuds are generic earbuds from commodity earbud-style headphones that are widely available and of negligible cost. The final construction of the current model can be seen in Fig 1C.

Costs in Table 1 were calculated using the density of PA757 ABS (1.05 g/cm³)³³ and the part weight, which is calculated using version 1.3.0-dev of the Slic3r software (https://slic3r.org, Italy). We assumed the price of 12 lbs (5.4545 kg) of virgin PA757 ABS pellets to be $38.99 USD³⁴. Commercial ABS filament was assumed to cost $23.96 USD/kg³⁵. Electricity costs were estimated using the Ontario Energy Board's current mid-peak rates³⁶,³⁷ multiplied by the printer's expected electricity use based on measurements of a similar printer with similar temperatures³⁸ printing for four hours then multiplied by 0.8 for an approximate conversion to US currency. This number was rounded up to the nearest cent. The energy costs of filament extrusion are negligible when estimated based on previous reporting³⁹ and were thus not included.

Acoustic transfer

The frequency response of Glia model stethoscopes, compared with the Littmann Cardiology III, was determined using an experimental setup modeled from a phantom-based frequency response setup previously described¹⁹. A latex balloon filled with 2 L (2000 g) of water was used as a phantom and each stethoscope was applied to the surface by hand. Phantom excitations were supplied by an external vibrating speaker which was placed in contact with the balloon and sound was played at 86 Hz intervals between 0 and 5000 Hz (white noise) for 15 seconds. The output of each stethoscope was recorded by a microphone which was placed in a silicon tube attached to the stethoscope head for spectral analysis. Spectral analyses such as these have been used successfully in the past to analyze breath sounds recorded from individuals with lung pathology⁴⁰. The simplicity of this design was intended to allow other users to validate our design independently.

# Results

After many iterations, we successfully designed a working stethoscope, known as the Glia model (Fig 1), at a total cost of $2.83 USD using recycled ABS pellets. A bill of materials and cost breakdown can be found in Table 1.

Item | Dimensions (mm) | | Weight (g) | | Cost using ABS pellets (USD) | | Cost using ABS filament (USD)
Stethoscope head | 44.30 x 62.45 x 17.80 | | 23.82 | | $0.17 | | $0.57
Stethoscope Y piece | 70.89 x 29.94 x 9.00 | | 2.84 | | $0.02 | | $0.07
Stethoscope ear tubes | 170.79 x 83.62 x 5.80 | | 12.52 | | $0.09 | | $0.30
Stethoscope ring | r = 21, h = 7 | | 0.81 | | $0.01 | | $0.02
Stethoscope spring | 91.25 x 111.62 x 15.05 | | 8.05 | | $0.06 | | $0.19
Silicone tubing | L = 400 – 12 OD, 8 ID 2 x L = 90 – 6 OD, 4 ID | | | | $1.93 | | $1.93
Diaphragm | r = 20 | | | | $0.06 | | $0.06
Silicone earbuds | n/a | | | | $0.02 | | $0.02
Electricity usage | 0.5 KWh at mid-peak rates | | | | $0.04 | | $0.04
Total | | | | | $2.40 | | $3.20

Table 1. Bill of materials for the Glia model stethoscope (100% infill)

We compared the Glia stethoscope to the Littmann Cardiology III using a phantom, as described in the methods. At all frequencies tested, the Glia model performed similarly to the Cardiology III (Fig 2A). The difference in attenuation (dB) of the Glia model to the Littmann Cardiology III is shown in Figure 2B with values greater than 0 dB indicating that the Glia attenuated less sound.

Figure 2. Calibration and comparison of 3D printed Glia model stethoscopes to the Littmann Cardiology III. Stethoscope output responses were measured using the equipment setup described in the methods. Each stethoscope model recorded input sound at multiple frequencies and the change in amplitude between input and recorded sound was documented (lower log attenuation is better) for each stethoscope (Figure 2A). The decibel difference in attenuation (Glia minus Littmann) is shown across all frequencies tested where values above 0 dB indicate the Glia model attenuated less sound (Figure 2B).
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

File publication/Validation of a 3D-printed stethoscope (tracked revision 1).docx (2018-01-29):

# Validation of an effective, low cost, Free/open access 3D-printed stethoscope

Alexander Pavlosky¹, Jennifer Glauche⁶, Spencer Chambers¹, Mahmoud Al-Alawi⁵, Kliment Yanev⁶, Tarek Loubani¹,²,³,⁴,⁵*

¹ Faculty of Medicine, University of Western Ontario, London, Ontario, Canada.

² Division of Emergency Medicine, Department of Medicine, University of Western Ontario, London, Ontario, Canada.

³ Division of Emergency Medicine, London Health Sciences Centre, London, Ontario, Canada

⁴ Division of Emergency Medicine, Al-Shifa Hospital, Gaza

⁵ Glia, Inc., London, Canada

⁶ No institutional affiliation

* Corresponding author

E-mail: tarek@tarek.org

# Abstract

The modern acoustic stethoscope is a useful clinical tool used to detect subtle, pathological changes in cardiac, pulmonary and vascular sounds. Currently, brand-name stethoscopes are expensive despite limited innovations in design or fabrication in recent decades. Consequently, the high cost of high quality, brand name models serves as a barrier to clinicians practicing in various settings, especially in low- and middle-income countries. In this publication, we describe the design and validation of a low-cost open-access (Free/Libre) 3D-printed stethoscope which is comparable to the Littmann Cardiology III for use in low-access clinics.

# Introduction

Since its introduction in 1819 by René Laennec¹, the acoustic stethoscope has been an integral part of clinical medicine. Despite the lack of major structural design innovations over recent decades, modern stethoscopes can be an expensive part of the physician’s armamentarium, often costing several hundred US dollars. The high cost of modern stethoscopes remains a significant barrier to physicians practicing in some developing countries, where few affordable high-quality options exist. Traditionally, the selection of a stethoscope often does not involve the acoustic properties of the model² with most users selecting an expensive brand-name stethoscope such as the Littmann Cardiology III. . However, previous studies which have compared stethoscope brands have concluded that cost does not correlate with better diaphragm sound quality at relevant frequencies, compared with lower-cost alternatives³,⁴. While other 3D printed stethoscope models that would be low-cost to produce can be found online, we are not aware of any that have been used clinically or research-validated.

Numerous groups have previously attempted to standardize methods to determine the efficacy of acoustic stethoscope models²,⁵⁻⁹, but currently no accepted standardized modality exists. Consequently, the performance of any acoustic stethoscope is little more than the manufacturer’s claim or the subjective opinion of the user. Some groups have attempted to objectively compare acoustic stethoscope models and currently two competing methods of measuring frequency response exist. The first method uses air coupling to transmit frequencies ²⁻⁶ while the other uses a phantom to simulate vibrations of the chest wall⁸,¹⁰,¹¹. These methods allow investigators to quantitatively compare the sensitivity of a stethoscope model compared with another.

In this article, we describe the construction and validation of a low cost, Free/open access 3D printed acoustic stethoscope - referred to here as the ‘Glia model’. The aim of this research is to give low budget health care systems affordable access to an effective stethoscope for a cost under $5 USD. To achieve this, we utilized 3D printing, a technology which is advancing rapidly and becoming increasingly inexpensive. The flexibility of 3D printing technology also allows users to augment our design to fit their own needs. We also attempt to make our validation methods accessible and low cost, allowing others to validate our design independently with ease.

# Methods
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

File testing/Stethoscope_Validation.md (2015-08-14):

#Glia Stethoscope Validation Procedure
---
##Ideology
A stethoscope is a fundamental medical tool used by doctors worldwide to characterize heart and lung sounds. A spectral analysis of heart sounds has shown the frequencies of interest are 0-500Hz [1]. Similar analysis of respiratory sounds has shown the frequencies of interest are 0-2000Hz [2]. A stethoscope that can reliably transmit frequencies at these levels has the greatest potential to be diagnostically useful.

##Setup
There are many different stethoscope models made by numerous companies which each claim to have a superior product. Previous work by *Abella et al* objectively tested the acoustic properties of 6 different models by measuring the power spectrum of frequencies ranging from 37.5-1000 Hz to determine which stethoscope was most efficient at transmitting sound [3]. At the time of this testing (1992) the Littmann Cardiology II was found to have superior qualities.

More recently in 2008 *Finkelstein* expanded this evaluation to include a subjective component by having a group of clinicians use each model on numerous patients and rate the clarity and loudness of sound transduction. Coupling this rating with subjective data at this time it was found that the Littmann Cardiology III was the best device on the market [4].
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

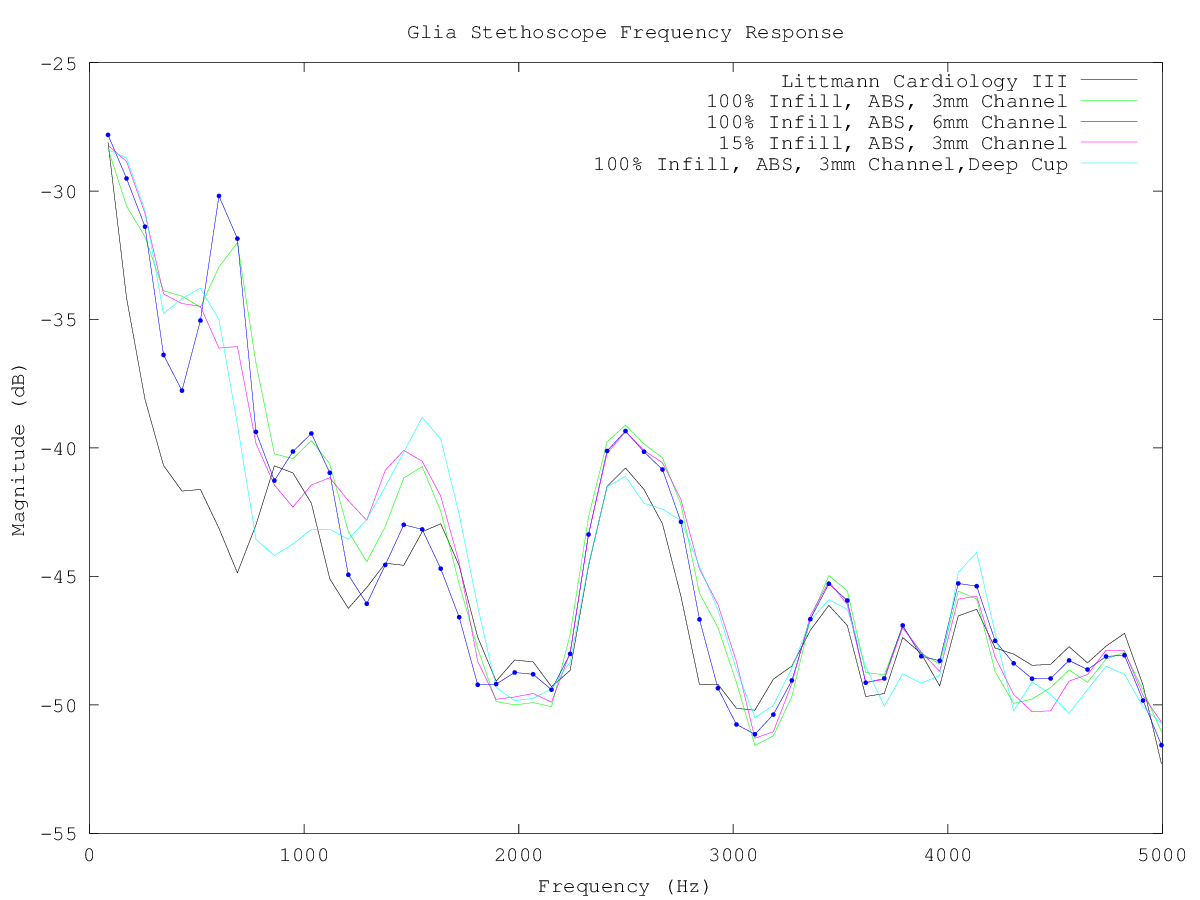
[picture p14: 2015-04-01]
testing/AllStethComp.png

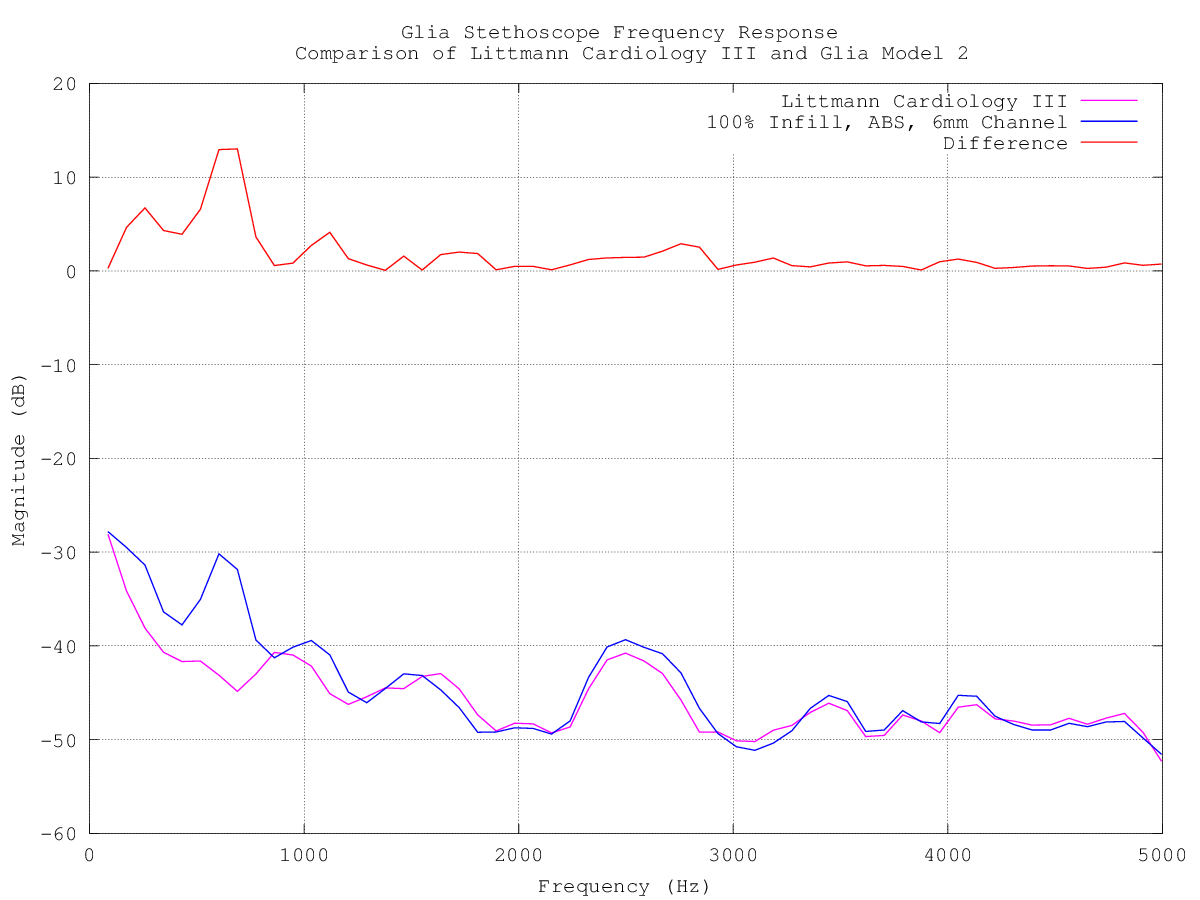
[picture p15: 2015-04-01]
testing/Litt3vsGlia2.png

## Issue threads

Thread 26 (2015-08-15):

### ISSUE TITLE
Enhancement request - bill of materials documentation

### ISSUE THREAD

**Issue by MarkRijckenberg** [GliaX/Stethoscope#26]
Hi,

Thanks for sharing this documentation!

A small suggestion: could you please improve the bill of materials section by adding the specific use/purpose, supplier number, order number and price of each bill of material item to make it clearer how much it all costs. Once it becomes visible for everyone, someone might find an alternative supplier that is cheaper with equal or better quality components.....

Here is an example: 

http://labs.nortd.com/lasersaur/bom-one-subsystems-eur

Regards,

Mark Rijckenberg

**Comment by tareko** [comment]
Thank you for this and for the example. I'll try to do a better job with it. Feel free to do it as well if you have the time. The only part with a real supplier here is the Staples folder binder. The rest are generically sourced.

tarek : )

**Comment by MarkRijckenberg** [comment]
I have sent you a pull request :-)

**Comment by tareko** [comment]
Done. I'm now working on adding the staples part (
http://www.staples.ca/en/Staples-Swing-Lock-Report-Cover-Clear-with-Black-Spine-5-Pack/product_780953_2-CA_1_20001
) and will make it into .MD in the readme

**Comment by MarkRijckenberg** [comment]
It would be even better if all those external parts could be replaced with 3D printed parts to lower the total cost. Isn't Picsima Technology or structur3d able to 3D print all the silicone components? I am just wondering....   Examples:   http://www.structur3d.io/#discov3ry   
and    http://www.picsima.com/#!3d-printing-silicone/cjg9

And an alternative to silicone for your components  might be Fila Flex as explained here: https://www.3dhubs.com/talk/thread/silicone-3d-printing      It has a certificate for use in medical situations.   See here:   http://recreus.com/en/4filaflex-filaments        Or maybe you already researched these possibilities?

**Comment by tareko** [comment]
Regarding the silicone, the *mold* is printed. No reason why we can't have an earpiece model, but I think it's more realistic in underfunded situations that they cannot easily switch between filament types (e.g., PLA/ABS to silicone). As such, the mold is printed and silicone (easily available in many places) is injected.

The moldable silicone you included is incorrect and I will ask @Joaz to correct it to what she used.

For now, closing this issue as I included the pull request. If you'd like to pursue the silicone issue further, please start a new issue for it.

tarek : )

**Comment by MarkRijckenberg** [comment]
OK, thanks for the clarifications and sorry about the "moldable silicone" error.

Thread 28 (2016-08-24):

### ISSUE TITLE
Size of rubber/silicone ring for diaphragm?

### ISSUE THREAD

**Issue by rickybloomfield** [GliaX/Stethoscope#28]
Do you have any specifications for the rubber/silicone ring we should purchase to hold on the diaphragm (similar to the other products you specified)? Thanks!

**Comment by tareko** [comment]
Thank you for commenting @rickybloomfield. I think @Joaz is best to comment, however, here are my thoughts:
Diaphragm should be about 40mm diameter with a middle slit. Total height is about 3mm. Up to now, I have just been grabbing whatever rings are available and testing them, but feel free to try some purchased ones and commenting on them.

tarek : )

**Comment by tareko** [comment]
@rickybloomfield If you have some suggested ring vendors, I could order a variety of rings and test to give my preferred.

tarek : )

**Comment by Joaz** [comment]
I was going to try it out, but with the 5€ on my bank account at the moment, I am unable to source and try different sizes/vendors.

**Comment by rickybloomfield** [comment]
This is why I'm asking - I have no idea where to start for "ring vendors" - it's just not something I've ever had to purchase before. :)

**Comment by tareko** [comment]
Let me think on it. In the meantime, I've used thick rubber bands that are doubled/tripled down. I'll take a photo of that. In looking at how to source from online, I think the terminology is "slotted o ring" or "slotted flat gasket", "square o ring". I see this page that looks most helpful:

http://www.theoringstore.com/index.php?main_page=index&cPath=367_98

Here, they call them "Square Orings also known as Tetraseals® or lathe-cut rings - Buna-N -Duro 70".

Perhaps I can call this group when they are open and check in?

Other examples:
http://www.ecstuning.com/ES1433022/
http://agenaastro.com/ahs-o-ring-2.html

**Comment by rickybloomfield** [comment]
Thanks! A photo would be awesome. I'm planning to construct one of these using parts sourced from the US Amazon store and post my results. I've already ordered the parts I think will work, with the exception of the ring.

**Comment by Joaz** [comment]
I am wondering if it would be possible to cut a groove into standard o-rings to a specific depth. I could rig up the edge of a razor blade using a precisely printed holder to make a cut at a specified depth.

**Comment by rickybloomfield** [comment]
Just curious if you could post that photo? I now have the printed parts from this site and am anxious to assemble. Only other issue is that you mention the T-piece in the instructions, but I don't see it anywhere else. Was that a purchased part?

**Comment by tareko** [comment]
I apologize - I am still travelling and have not yet had a chance. However, here is the T/Y piece:
https://github.com/GliaX/Stethoscope/blob/master/stethoscope_head/output/YPiece_output.stl

I don't like it much myself, and would rather see something like this:
http://www.thingiverse.com/thing:577507 (see last model)

Regarding O-Rings, I called the O ring store, and confirmed that probably the best way to do this with purchased O-Rings is to get the 40mm O-Ring and put a midline slit. I cannot test this for another 4 weeks until I'm back in Canada, but happy to order some your way if you'd like to test it out.

tarek : )

**Comment by rickybloomfield** [comment]
Got it, thanks. I'll print out that piece. I'll also note that the recommended tubes to connect the Y-piece to the ear tubes are way too small. They are the same diameter as the ear tubes themselves, so they don't fit around it. I'll have to order some more of a larger size.

I'd be happy to test the O-rings, but unfortunately I don't have a tool to add the midline slit, which I'd probably need to do it right (i.e., without destroying the O-ring).

Thanks for your help!

**Comment by Joaz** [comment]
@rickybloomfield I have about 2 good ideas for that in my head, need to source new o-rings to make it happen and test it. Feel free to bribe me in order to accelerate that process.

**Comment by tareko** [comment]
@rickybloomfield Please take a look at the [new design of the head](https://github.com/GliaX/Stethoscope/blob/master/head.stl) based on [this commit](https://github.com/GliaX/Stethoscope/commit/a2abf1494062dd74f7cbb66e07adb827aaf49a68) which is expanded on in the [pull request](https://github.com/GliaX/Stethoscope/pull/34).

This will completely denecessitate the o-rings, which we have found hard to source in many parts of the world.

As such, I'm closing this thread as resolved.

tarek : )

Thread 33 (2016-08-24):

### ISSUE TITLE
Size of Diaphragm

### ISSUE THREAD

**Issue by DaveZA** [GliaX/Stethoscope#33]
Thanks for the design - this is our new home project.

Sorry if this sounds like a dumb question, but nowhere do I see the diameter of the Diaphragm.

Is it supposed to sit inside the lip on the top of the head ?
Does it extend to the inner edge of the ring ?
Should it be glued to the lip, or does it need to have some play between the lip and the ring ?

**Comment by tareko** [comment]
Hi @DaveZA!

Amazing that you've taken an interest in this! Short answer: 40mm diameter.

**However**, before you get too far, please take a look at the [new design of the head](https://github.com/GliaX/Stethoscope/blob/master/head.stl) based on [this commit](https://github.com/GliaX/Stethoscope/commit/a2abf1494062dd74f7cbb66e07adb827aaf49a68) which is expanded on in [this pull request](https://github.com/GliaX/Stethoscope/pull/34).

This will completely denecessitate the o-rings, which we have found hard to source in many parts of the world.

The design is more than good enough to be our default, so I merged it into the master branch today.

Let me know if you have any questions.

tarek : )

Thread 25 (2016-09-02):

### ISSUE TITLE
Earplug mold should have direction marks

### ISSUE THREAD

**Issue by Joaz** [GliaX/Stethoscope#25]
... to see easily which side is the correct one to bolt it on.

**Comment by tareko** [comment]
@Joaz, any need to revisit this issue? Or shall we leave and close?

**Comment by Joaz** [comment]
Are you actually using that part for production or are you rather using 3rd party earplugs?

**Comment by tareko** [comment]
3rd party. However, it would be nice to leave this option open to those who need it. It sounds like it's not a big enough concern that we should modify this, but rather just close and leave people to sort it out if they use this method.

**Comment by Joaz** [comment]
Yes. This was an annoyance only, it works perfectly without them.

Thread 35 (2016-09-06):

### ISSUE TITLE
eartube file

### ISSUE THREAD

**Issue by j0en0** [GliaX/Stethoscope#35]
I'm having a few issues with the eartube file, the segments don't seem to be meshed together properly and they come out separate in the output file. The source file for eartube isn't in the master folder. Is there a way to get the source file? 
Regards

**Comment by tareko** [comment]
Hello @j0en0,

Could you take some screenshots or describe how to create this? Are you using the "eartube.stl" file in the base directory of the repo?

The source file is created like [here](https://github.com/GliaX/Stethoscope#changing-and-creating-scad-files), I believe.

@Joaz I vaguely recall that when I looked we were missing the final eartube file? Could you double-check?

@alawx did make an OpenSCAD version of the eartube. @Alawx: Could you upload it?

tarek : )

**Comment by j0en0** [comment]
Hi @tareko 

Yup, I am using the "eartube.stl" file from the master branch of the base directory. I have attached the screen shots. 
Thanks
Jono
[screenshots.pdf](https://github.com/GliaX/Stethoscope/files/457576/screenshots.pdf)

**Comment by tareko** [comment]
Interesting. Which slicer?

**Comment by redsqrly** [comment]
Hey @tareko,

Im printing the model for @j0en0 and having the issues with the eartube.stl. Im using Simplify3D, ive tried to find a way to fix it in Meshmixer but all i know is that it isnt a non-manifold issue. The min thickness tool highlights a number of areas also. 

Kind regards,
Kirill

**Comment by tareko** [comment]
@redsqrly: Thank you for the information. Do you mind trying to slice with [Slic3r](http://slic3r.org) and telling me what happens? @Joaz Any thoughts?

I usually use slic3r and haven't had issues with the model myself.

**Comment by redsqrly** [comment]
@tareko No probs! Worked in Slic3r, i can see a couple of voids in infill in two or so layers but the walls are solid. I used to swear by Slic3r and love the fact its opensource but Simplify3D is just that little bit more efficient, i think. 
The stl file looks completely smooth in Slic3r, yet in Meshmixer and Simplify3D each individual segment is visible, and i can actually separate them as 3 individual shells but not all the segments become shells, just the 3 so its impossible to move all of them closer together.

**Comment by tareko** [comment]
Interesting. Can we consider this issue closed, or do you think there's something we can do with the STL to decrease the odds of this issue?

**Comment by redsqrly** [comment]
I was thinking that the issue is with the mesh thickness as Meshmixer's thickness analysis tool highlights a number of areas which are below 0.5mm. 0,5mm is the minimum thickness i can manage due to my nozzle size but i believe 1mm minimum shell thickness is recommended for 3d printed models. Do you still have access to the original design file, would that be SCAD? And if so, could you try to adjust the shell thickness through OpenScad or try to generate the file again in case there was an error?

**Comment by redsqrly** [comment]
![eartube mesh](https://cloud.githubusercontent.com/assets/11467948/18290608/150fd97e-747c-11e6-8b84-5e33ea7d0330.JPG)

**Comment by tareko** [comment]
OK, I will close this unless @Joaz has something to say about the matter. I'll add a note that it's a known issue.

**Comment by redsqrly** [comment]
@tareko ive ended up redrawing the eartube using the original stl for dimensions as the issue was still bugging me, pun intended :) Ive uploaded it to my fork, feel free to add it to your files if you'd like. The shape is almost the same, as close as i could get, and the dimensions are exactly the same.

**Comment by tareko** [comment]
Thank you for this. What was your model made in? I see the STL in your tree, but not the source file.

**Comment by redsqrly** [comment]
No probs, i used Autodesk's Fusion 360, what format would you like the source to be in?

**Comment by redsqrly** [comment]
![tube differences](https://cloud.githubusercontent.com/assets/11467948/18313743/fda2e588-7507-11e6-94b3-84baa11c54fa.JPG)

It came out a little shorter as the spline was a couple of degrees out. This wont affect the performance, will it?

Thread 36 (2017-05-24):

### ISSUE TITLE
Alternative material to Acrylonitrile butadiene styrene plastic?

### ISSUE THREAD

**Issue by abitofalchemy** [GliaX/Stethoscope#36]
What might be the best alternative material to Acrylonitrile butadiene styrene (ABS) plastic?

**Comment by tareko** [comment]
PLA also works well. What is available to you?

**Comment by abitofalchemy** [comment]
Great, PLA is available for all parts except for the eartube, which is only available in "frosted extreme" plastic from shapeways.com. It's due to what their "model checks" that auto determines the material options as the files are uploaded.

**Comment by tareko** [comment]
What are you trying to do? Print through a service like shapeways? perhaps 3dhubs or your local makerspace might be able to help for cheaper? Please do let me know how it works out either way!

tarek : )

**Comment by abitofalchemy** [comment]
I want to build a pair (or two) to bring down to Haiti. I will check out 3dhubs, I hope they can do 100% infill. Yes, I'll let you know how it goes. Thank you!!

**Comment by abitofalchemy** [comment]
Do you have a specific shop on 3dhubs that you were satisfied with the quality of the Head?

**Comment by tareko** [comment]
Two pieces here:
1. Unless you are a physician, please be very cautious about using a stethoscope that has not been built in a proper proper way and tested.

2. We don't have a preferred 3DHubs person, but when you do make a connection, feel free to share this page / my contact information so I can make sure they produce properly.

tarek : )

**Comment by abitofalchemy** [comment]
Tarek,

(BTW if you think I should email you directly instead, let me know)

I am building one for a physician. I went on 3DHubs and found a maker that
can build it, but he cautioned that the 90 deg port (on the Head) could
break if it falls and receives impact. Also he recommended an ABS HighDef
Resin to achieve 100% infill and the added benefit that it will be sturdy.

Another issue raised was the wall thickness of the Head's right-angle port.
If the inner radius is kept as is, the wall can be increased from 1.0mm to
1.5mm, right?

**Comment by tareko** [comment]
I think these conversations are best had in public, so let's continue here.

I don't think you need to worry about the integrity of the port. The part is essentially indestructible (we even did hammer tests), and definitely won't break with a fall. Also, once inside a tube, there is almost zero chance that it fall in a way where that part has to take a load.

Overall, I would suggest printing as is. It hasn't been tested any other way.

tarek : )

**Comment by abitofalchemy** [comment]
Question about the earplug mold. Is it a two piece part? If so what is the upper part for? (the one with holes that go all the way through) 
And, the material for the earplug mold should be hard plastic? It is a mold to be used with "Silicone for ear plugs" so that these earplugs are molded on this earplug_mold.stl part? The earplug model is not meant to be printed in silicon material, right?  // Sal :)

**Comment by tareko** [comment]
This part is no longer needed at this point. You can use any commodity ear piece from low-cost earbuds. Something [like this](https://www.encoredataproducts.com/images/products/secondary/g-er-215-500-1.jpg).

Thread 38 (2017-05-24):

### ISSUE TITLE
Dimensions and drawings for non scad users?

### ISSUE THREAD

**Issue by yongkimleng** [GliaX/Stethoscope#38]
I would like to make customizations/modifications to the design but not doing very well with SCAD (super slow for some reason). The STL gives errors while being imported into Solidworks, so I figure that it would be easier if I could re-design from scratch given the dimensions.
If it would be possible to also upload a pdf of drawing dimensions, it could help others as well :)

**Comment by tareko** [comment]
Hi @yongkimleng,

Thank you for this. I don't have the dimensions handy and I think we have to commit resources to other things at the moment. However, why not print one and grab a digital caliper to measure? That should get you most of the way there. Otherwise, we don't use or support any non-Free software tools in the project, so we can't really help with Solidworks.

Have you looked through the crystalCAD file? It should give you enough measurements to figure things out with a bit of work.

I'm going to close this issue as 'wontfix', but please feel free to comment further as desired. If you do end up making some drawings, please submit a PR to share them with others.

tarek : )

**Comment by yongkimleng** [comment]
I don't really have a printer, usually get my designs machined out of engineering plastic. I've been through like 2 different software which supposedly read scad files but they have been glitching out. Do let me know if anyone had success with something which works on Windows.

If someone in the community can grab a simple hand drawing, phone-captured photo of drawings or something, I can digitize it into a nice drawing too.

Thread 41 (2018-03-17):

### ISSUE TITLE
Ear tube & Y-piece outer diameter?

### ISSUE THREAD

**Issue by abitofalchemy** [GliaX/Stethoscope#41]
1. The tube connecting the eartube to the Y-pieace is called for it to be 20cm long in the list of materials, but if I look at the [sample in FB](https://www.facebook.com/photo.php?fbid=148469625666800&set=pb.100015112902901.-2207520000.1497223194.&type=3&theater) it looks shorter, is 20 cm is till the length to go with?
2. I had a really hard time with the outer diameter of ear-tubes and Y-piece  and the 4mm inner diameter/6mm OD tubing. It seems to me that this tubing should have a wider ID or the Y and ear-tubes be smaller in diameter. What do you think?  Look at the connecting points on my [current prototype](https://flic.kr/p/Vs68qJ)

**Comment by tareko** [comment]
Hi @abitofalchemy,

Congratulations on making the stethoscope! Regarding your questions:

1. Yes, 20cm is really the maximum. If you want to wear it around your neck, that may even end up being a bit short., since the decreased weight will not properly hold down the stethoscope and it will jut to the sides.
1. I strongly suggest the 4/6 and that is what we have tested with and is validated. However, if you want 6/8, there should theoretically be no deterioration.

It strikes me that it's possible you are using PVC and not Silicone tubing. PVC tubing has not been tested and it is unlikely that it will work. Is that perhaps why you're having such a hard time hooking it up?

**Comment by ajithmel** [comment]
that is very good and i like what you guys are doing, thank you

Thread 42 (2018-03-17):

### ISSUE TITLE
Decide on a license

### ISSUE THREAD

**Issue by pinobatch** [GliaX/Stethoscope#42]
In [this story on SoylentNews about the stethoscope design](https://soylentnews.org/article.pl?sid=18/03/16/0245209), editor "cmn32480" wrote:

>[Ed: as of posting there is no license on the Github documents. Thus as per the Berne Convention it is not yet freely available, until explicitly published under an open license such as CC or similar. ]

Under what license will these plans be made available? The GNU project maintains a [list of licenses for designs of physical objects](https://www.gnu.org/licenses/license-list.en.html#Designs).

**Comment by tareko** [comment]
Hi,

I've added the TAPR OHL, which is the license we always intended. Thank you for pointing out the oversight. As you probably know, copyright does not apply to hardware, and the Berne convention does not apply to this or any hardware. Even its application to design files like SCAD files is tenuous at best. Hardware is usually protected by trade secrets, patents and trademarks, not copyright.

The Open Source Hardware Association has some information on this, as well as some various sources online.

In any case, it was definitely an oversight, as it seemed so obvious to us that it was open source : ) Added and thank you!

tarek : )

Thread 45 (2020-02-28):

### ISSUE TITLE
Spring is too tight when printed in PLA

### ISSUE THREAD

**Issue by tareko** [GliaX/Stethoscope#45]
The spring is too tight initially and needs significant softening to work properly.

**Comment by mrjohnc** [comment]
I loosened mine by softening the curved part of it in near boiling water for some seconds and then bending a little till it cooled, although this could be done too much and make the part useless. It seems important to get this right because PLA is the most commonly used printing material.

One suggestion would be to put some bends into the curved section to make it more springy, like how this spring works

https://www.youmagine.com/designs/parametric-spring

**Comment by sbamueller** [comment]
the spring is so tight its difficult to fit the ear pieces. I'm just trying with a 105% size, maybe this will help.

**Comment by tareko** [comment]
@sbamueller: Which model are you using? This should not be printed in PLA, and should be fine at this point. Could you post a screenshot of the STL you're using? Is it [this one](https://github.com/GliaX/Stethoscope/blob/master/source_files/stl/spring.stl)

**Comment by sbamueller** [comment]
last try was with 105%

![grafik](https://user-images.githubusercontent.com/24292608/75594639-ad231b80-5a89-11ea-8f75-fccb25ebc1cf.png)
with that it seems to work.

**Comment by tareko** [comment]
OK, great that you started from the 3mf!!!! Glad that it works. Sometimes indeed it needs a bit of scaling up or down..

**Comment by tareko** [comment]
I'm going to close this issue. re-open if anything remains.

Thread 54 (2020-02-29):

### ISSUE TITLE
ear plugs

### ISSUE THREAD

**Issue by sbamueller** [GliaX/Stethoscope#54]
I bought the xcessor ear plugs but those don't seem to fit with the ear tubes. Which type should I buy?

**Comment by tareko** [comment]
[These are the ones we use](https://www.amazon.ca/gp/product/B006VELFJY)! Sounds like you got the same. Could you post a short video / photo of the issue?

Also, not sure if you saw the [assembly video](https://glia.org/stethoscope), but it might be of help if you haven't?

**Comment by sbamueller** [comment]
[These are the one](https://www.amazon.de/gp/product/B07DJ58BJK/ref=ppx_yo_dt_b_asin_title_o00_s00?ie=UTF8&psc=1)s I got from German Amazon. But I'm not really able to fit them around the IIIIII::::II 

Maybe its me?
I can fit the ones I still have from my MDF Stethoscope.

![A8F9BDAC-2204-433E-9DE8-5E8E171EB7E7_1_105_c](https://user-images.githubusercontent.com/24292608/75594138-0ab66880-5a88-11ea-8cba-9bd1ee950580.jpeg)

**Comment by tareko** [comment]
those look right. Two options:

1. What we do at glia is just exercise some patience and wrap it around. Once fitted, it sits well but can come undone, in which case crazy glue is routine for us.

2. You could take a file and file down the outer ring a bit so that the fit is smoother.

p.s., those prints look great.

**Comment by sbamueller** [comment]
I'll try that, thanks for your help

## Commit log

2014-12-02 initial commit with some notes and the begin of a basic sketch
    [stethoscope_head.scad]
2014-12-05 finished outside dimensons without tube exit
    [stethoscope_head.scad]
2014-12-19 flat cuts of the lower section + a set of measurements
    [stethoscope_head.scad]
2015-01-08 converted the measurements into a cone and noticed that I need to retake the measurements
    [stethoscope_head.scad]
2015-01-17 implementing inner shape from lathe measurements
    [stethoscope_head.scad]
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2015-01-27 connector attached to the head
    [stethoscope_head.scad]
2015-01-27 first printable version of the stethoscope head, now ready to test print
    [printable_head1.scad, printable_head1.stl]
2015-02-03 add hole diameters for 3d printing
    [printable_head1.scad, printable_head1.stl]
2015-03-30 trying out printable head #2
    [printable_head1.scad, printable_head2.stl]
2015-03-31 Eartube for Stethoscope
    [eartube.stl]
2015-04-01 Printable head #4 with cylindrical tube connector
    [printable_head4.stl]
2015-04-02 made a better shaped eartube
    [eartube.stl]
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2015-06-12 added copies of 'current' files for use to make a working stethoscope.
    [head.stl]
2015-06-14 silicone fillable y piece
    [YPiece_output.stl]
2015-06-14 fixed nut supports
    [YPiece_output.stl]
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2015-06-14 redesign of the y piece
    [YPiece_output.stl]
2015-06-15 next iteration of earplugs, ypiece
    [YPiece_output.stl]
2015-08-15 Add bill of materials for hardware purchased via an external supplier. File is a Libreoffice 5.0 spreadsheet file. A few entries are still missing the order URL and price.
    [bill_of_materials-non_3D_printed_hardware-libreoffice_5_spreadsheet.ods]
2015-08-15 Bill of materials clean-up
    [Bill_of_materials.ods, bill_of_materials-non_3D_printed_hardware-libreoffice_5_spreadsheet.ods]
2015-09-02 tube function its a function that generate a tube , takes inner,outer diameters and the length then generated centerd at 0,0,0
    [stethoscope y pice.scad]
2015-09-02 the cylender are smoother
    [stethoscope y pice.scad]
2015-09-02 three tubes in angels
    [stethoscope y pice.scad]
2015-09-02 Added connecting shape and channel
    [stethoscope y pice.scad]
2015-09-11 y-peace with support
    [stethoscope y pice.scad]
2015-09-14 Rename file and place in separate directory
    [stethoscope-y-piece.scad]
2015-10-14 Add STL of y piece
    [y_piece.stl]
2015-10-14 Removed old Y piece.
    [YPiece_output.stl]
2016-06-13 Update Y piece
    Remove supports
    Thicken wall
    [stethoscope-y-piece.scad, y_piece.stl]
2016-06-15 Update to latest (and now correct) Y-piece
    Properly comment Y Piece
    [stethoscope-y-piece.scad, y_piece.stl]
2016-07-06 Add files via upload
    Spring/bridge
    [spring_round.stl]
2016-07-06 Add stethoscope ring to replace need for flat washer
    [stethoscope_ring.scad, stethoscope_ring.stl]
2016-07-06 Move all source files into source_files directory
    This will more clearly distinguish files for printing from source files for tinkering
    [printable_head1.scad, printable_head1.stl, printable_head2.stl, printable_head4.stl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]
2016-07-06 Update spring_round.scad
    -m "Add OpenSCAD file for printable stethoscope spring"
    [spring_round.scad]
2016-07-06 Clean up source code; insert proper comments
    [spring_round.scad, spring_round.stl]
2016-07-06 Add printable stethoscope spring that slides between eartubes
    [spring_round.stl]
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2016-07-13 Prune and clean old files so only current version is available.
    [earplug_mold.scad, printable_head1.scad, printable_head1.stl, printable_head2.stl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]
2016-08-24 Integrate ring into head (#34)
    * Integrate ring into head
    This also undoes use of the square o-ring, which has proved very difficult
    to find.
    * Delete spring_round from inappropriate directory
    * Change stethoscope head to fn=365 for smoother look
    * Use head of integrated ring
    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
    [ring.stl, spring_round.stl, stethoscope_head-ring.scad, stethoscope_head.scad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]
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2016-11-05 Updated spring by @Alawx with some cleanup and comments added
    [stethoscope_spring.scad]
2016-11-05 Properly rotate spring holes and reduce size to make a press fit.
    [spring.stl, stethoscope_spring.scad]
2017-02-07 Add second leaf to spring and prettify
    [spring.stl, stethoscope_spring.scad]
2017-02-10 Add rounded eartube
    [stethoscope_eartube.scad]
2017-02-10 Update eartube to permit earbud connector. Update spring
    [stethoscope_spring.scad]
2017-02-10 Removed superfluous files
    [stethoscope_eartube.stl, stethoscope_spring.stl]
2017-02-10 Add STLs of new eartube and spring from commit fa080f4bb13bf7deb5e0e1cf8c6ea7379ec32127 and cee863869a59e68ca617e20c751dd633e227266f
    [spring.stl]
2017-02-27 added tourniquit design files
    [touniquit.scad, tuniquit_rod.stl, tuniquit_strap.stl]
2017-02-27 Remove Tourniquet files
    [touniquit.scad, tuniquit_rod.stl, tuniquit_strap.stl]
2017-02-27 Add holder for metallic springs
    [stethoscope_metallic_spring_holder.scad]
2017-04-18 testing on ear tube to rempve the curve in the rear bud
    [stethoscope_eartube.scad, stethoscope_eartube.stl]
2017-04-18 Moved into correct locations
    [eartube.stl, stethoscope_eartube.scad, stethoscope_eartube.stl]
2017-04-18 fixing the earbud of the ear tube by removing the curvy edge
    [stethoscope_eartube.scad]
2017-04-18 fixed eartube
    [eartube.stl]
2017-04-18 sharo edges holds the earbud
    [eartube.stl, stethoscope_eartube.scad]
2017-04-19 bug fixed
    [eartube.stl, stethoscope_eartube.scad]
2017-04-20 wider cylinder to hold the earbud
    [eartube.stl, stethoscope_eartube.scad]
2017-04-21 Comment out inner spring
    [spring.stl, stethoscope_spring.scad]
2017-06-19 Remove ringed head and replace
    [stethoscope_head-ring.scad, stethoscope_head.scad]
2017-06-19 Remove earplug mold - deprecated
    [earplug_mold.scad]
2017-06-20 Add assembly manual
    [head_with_ring.scad]
2017-07-01 adding single-fit to the eartube
    [eartube.stl, spring.stl, stethoscope_eartube.scad, stethoscope_spring.scad]
2017-08-05 make smoother end of the eartube "insert" and END_KEY to stop it from entering the spring
    [eartube.stl, spring.stl, stethoscope_eartube.scad, stethoscope_spring.scad]
2017-08-07 Revert "make smoother end of the eartube "insert" and END_KEY to stop it from entering the spring"
    This reverts commit c7f182dbf284bb738c27f1de774f66863b80bafc.
    [eartube.stl, spring.stl, stethoscope_eartube.scad, stethoscope_spring.scad]
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2017-08-20 adding mouse ears for weak ends
    [eartube.stl, stethoscope_eartube.scad, stethoscope_head.scad]
2017-08-24 adding the ability for making the walls thicker and adding a key
    [stethoscope_spring.scad]
2017-08-24 thicker walls for the holes of the spring
    [spring.stl, stethoscope_spring.scad]
2017-10-08 edited earmouse for eartube for easier remove
    [eartube.stl, stethoscope_eartube.scad]
2017-10-09 adding connector to the mouse ears
    [eartube.stl, stethoscope_eartube.scad, stethoscope_head.scad]
2017-11-04 adding and modifyiong mouse ears for the head and /y-piece
    [eartube.stl, stethoscope_eartube.scad, stethoscope_head.scad, stethoscope_y-piece.scad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]
2017-11-28 Create 2mm distance from eartube to mouse ear
    [eartube.stl, stethoscope_eartube.scad]
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2019-01-10 Straighten and unrotate eartubes and relax spring (#48)
    * Modify eartube to point less downward into ear canal. This should address Issue #44
    * Straighten eartubes in spring
    * Only straighten eartubes, not loosen spring
    * Looser spring. This should solve Issue #45
    * Reduce overhang of spring
    [eartube.stl, spring.stl, stethoscope_eartube.scad, stethoscope_spring.scad]
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2019-02-20 Add Plate with 4 stethoscopes for Slic3r
    [stethoscope_x4.3mf]
2019-06-01 Update to most current version
    [eartube.stl, spring.stl, stethoscope_eartube.scad, stethoscope_spring.scad]
2019-07-11 Reorganize so that STLs are a bit more hidden and 3MF files are more prominent, making it more likely that people will print the correct files
    [eartube.stl, ring.stl, ring_x16.3mf, spring.stl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]
2019-07-11 Remove obsolete files
    [stethoscope_x4.3mf]
2019-07-11 This is incorporated into README, so removed
    [Bill_of_materials.ods]
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2019-08-19 Reorganize so that STLs are a bit more hidden and 3MF files are mor prominent, making it more likely that people will print the correct files
    [Head Diaphragm Template(Cutting Guide).scad]
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2019-12-09 Revert "resort files location"
    This reverts commit 4fe4cde23c22dceadeb0101f6225a092ccdacd6f.
    [Head Diaphragm Template(Cutting Guide).stl, stethoscope_eartube.stl, stethoscope_ring.stl, stethoscope_spring.stl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]
2019-12-09 Revert "resort files location"
    This reverts commit abf3eab0864790c0e46fefdd01405c819544aaf0.
    [Head Diaphragm Template(Cutting Guide).scad, Head Diaphragm Template(Cutting Guide).stl, eartube.stl, ring.stl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]
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
